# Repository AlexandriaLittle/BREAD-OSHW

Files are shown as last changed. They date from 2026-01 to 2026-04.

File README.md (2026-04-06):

# BREAD - Broadly Reconfigurable and Expandable Automation Device

## How to use
**Please check the Documentation folder for the original research paper and how-to guides!**

## Original Authors
The original project documentation is published in the open-access journal Hardware X 15 and is authored by Shane Oberloier, Nicholas G. Whisman, Finn Hafting, and Joshua M. Pearce. Other contributors have added to the body of work since. Please refer to the original sources (below) for important details about licensing, contributors, and any updates.

## About this repository
This is not an 'official' or even necessarily a current collection of all of these collected projects. Please see the links below to download from their original sources. The projects are collected here mostly for convenient access and learning.

## License
As the original project is licensed CC-BY-SA-4.0, this project is released under the same license. Social share image source https://www.appropedia.org/w/index.php?curid=122111.

## BREAD Links
- [Finn Hafting: Modularize your electronics with BREAD - YouTube](https://www.youtube.com/watch?v=OMPlVbqSqJ4)
- [Open Source Framework: Expandable Reconfigurable Data Acquisition Device (BREAD)](https://www.appropedia.org/Open_Source_Framework_for_a_Broadly_Expandable_and_Reconfigurable_Data_Acquisition_and_Automation_Device_(BREAD))
- [OSHE Bread Applications - Appropedia, the sustainability wiki](https://www.appropedia.org/OSHE_Bread_Applications)
- [GitHub - FHafting/BREAD](https://github.com/FHafting/BREAD)
- [OSF | BREAD](https://osf.io/u2h4g/overview)
- [OSF | LOAF_x04 Backplane](https://osf.io/7mk4w/overview)
- [OSF | BREAD LOAF_x08](https://osf.io/x4yqj/overview)
- [OSF | BREAD Slice - +/- 10A Current Sensor (SLC_CR10)](https://osf.io/ajmbe/overview)
- [OSF | BREAD Slice - +/- 20A Current Sensor (SLC_CR20)](https://osf.io/xe6cz/overview)
- [OSF | BREAD Slice - +/- 40A Current Sensor (SLC_CR40)](https://osf.io/xpgf8/overview)
- [OSF | BREAD Slice - 4 Channel Relay (SLC_RLAY)](https://osf.io/5vxws/overview)
- [OSF | BREAD Slice - Audio Analysis (SLC_AAFT)](https://osf.io/a8nk5/overview)
- [OSF | BREAD Slice - Bioreactor (SPECIALIZED) (SLC_PHDO)](https://osf.io/zbg98/overview)
- [OSF | BREAD Slice - BLDC Motor Controller](https://osf.io/w9rka/overview)
- [OSF | BREAD Slice - DC Motor Controller (SLC_DCMT)](https://osf.io/6aw9m/overview)
- [OSF | BREAD Slice - Field Solar Power (SLC_SOLR)](https://osf.io/9gm5h/overview)
- [OSF | BREAD Slice - MOLD(Mass Output and Logging Device)](https://osf.io/nm7je/overview)
- [OSF | BREAD Slice - Pressure Sensor](https://osf.io/86dz7/overview)
- [OSF | BREAD Slice - Pump Control Board (Specialized) (SLC_PUMP)](https://osf.io/4mzs8/overview)
- [OSF | BREAD Slice - Relay Heating Element Controller (SLC_RLHT)](https://osf.io/pf6gy/overview)
- [OSF | BREAD Slice - Servo Motor Controller (SLC_SERV)](https://osf.io/d7vks/overview)
- [OSF | BREAD Slice - Stepper Motor Controller (SLC_STEP)](https://osf.io/q8nkc/overview)
- [OSF | BREAD Slice - Template (SLC_TEMP)](https://osf.io/v5327/overview)
- [OSF | BREAD Slice - Text-to-Speech](https://osf.io/erbp6/overview)
- [OSF | BREAD Slice - Thermocouple Reader (SLC_THRM)](https://osf.io/sfehu/overview)
- [OSF | BREAD Slice - USB Port (SLC_USBP)](https://osf.io/j9rh5/overview)
- [OSF | BREAD Slice -- Analog Reader / FFT (SLC_LVAI)](https://osf.io/742ez/overview)
- [OSF | BREAD Slice -- Battery Management (SLC_BMS)](https://osf.io/yrmqu/overview)
- [OSF | BREAD Slice -- Buck Converter / Analog Signal Generator (SLC_BUCK)](https://osf.io/2xpnu/overview)
- [OSF | BREAD Slice-- Heating Element Controller (SLC_HEAT)](https://osf.io/m53fu/overview)
- [OSF | BREAD BUNS](https://osf.io/hbz92/overview)
- [OSF | BREAD CAN update](https://osf.io/3rnj4/overview)
- [OSF | BREAD DAQ](https://osf.io/wxt3s/overview)
- [OSF | BREAD Vision](https://osf.io/2htbm/overview)
- [OSF | Off-Grid BREAD](https://osf.io/98m6k/overview)
- [OSF | Integrated Open Source Pyrolysis Board based on BREAD](https://osf.io/3ugbn/overview)
- [Shane Oberloier | BREAD Contributor](https://osf.io/user/fntgd)
- [Nicholas Whisman | BREAD Contributor](https://osf.io/user/zs4mx?tab=2)
- [Finn Hafting | BREAD Contributor](https://osf.io/user/78mv4?tab=2)
- [BREAD References and Citations](https://ouci.dntb.gov.ua/en/works/lxXvAPQl/)
- [Open Source Hardware Enterprise](https://oshe.io/)
- [Original Project Logo](https://www.appropedia.org/w/index.php?curid=122111)

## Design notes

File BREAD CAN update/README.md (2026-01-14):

# BREAD Introduction

Welcome to the Broadly Reconfigurable and Expandable Automation Device (BREAD) project. This repository contains the files required to build your own supervisory control and data acquisition system or environmental sensing platform to suit your needs. Each function card, called a Slice, performs a specific function like temperature monitoring, DC motor control, relay control, etc. By linking Slices together with the Loaf backplane, you can create customized electronics to perform a variety of functions. This repository contains the bill of materials, board designs, 3D printable case design, and firmware examples for each Slice and the Loaf backplane.

## Navigating the repository

Each Slice and Loaf project is organized into the following files and subfolders:

-   Schematic.pdf: electrical schematic of the Slice in pdf format.
-   BOM_\<slice name\>.ods: bill of materials with links to purchase components on Digikey.
-   PCB Design: folder containing the KiCAD project files for the schematic and board design.
-   Gerbers: folder containing the gerber files extracted from the KiCAD board file. Use these files for manufacturing the PCB.
-   Firmware: folder containing examples and testing code unique to each Slice.
-   Mechanical: folder containing the 3D printable case files for each Slice.

## How to build a Slice

1.  Download all files from the Gerber folder. Compress files into a zip folder and upload to any PCB manufacturing company. If manufacturing the PCBs, use the “F_Cu.gbr” and “B_Cu.gbr” files for the front and back respectively.
2.  Order all components from the BOM file.
3.  Solder the components to the PCB starting with any SMD components and then through-hole components.
4.  3D print the case files using your favourite slicer.
5.  Assemble the case with the Slice hardware (finished PCB).

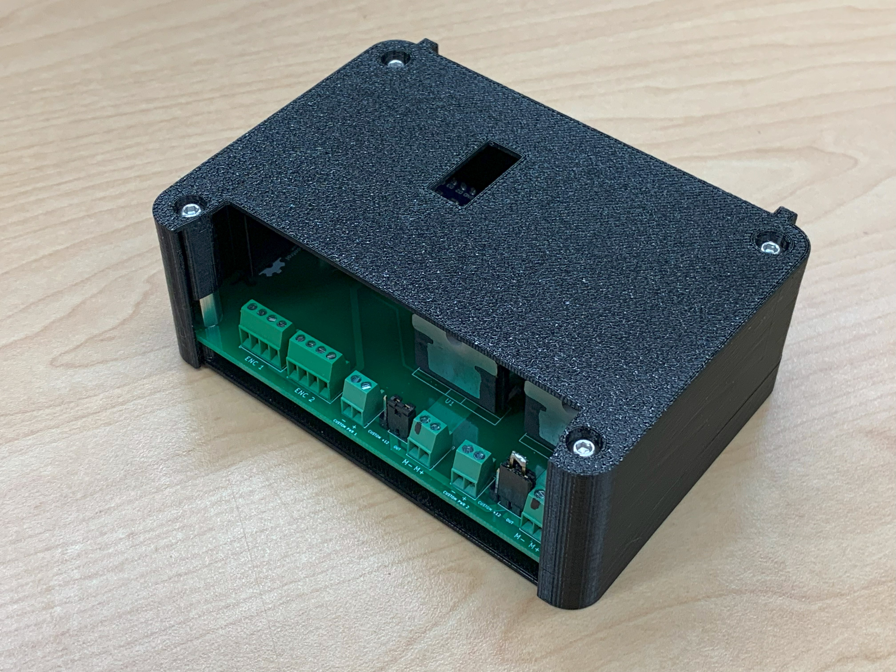
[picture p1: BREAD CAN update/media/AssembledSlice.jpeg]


## How to build the Loaf

Follow the same steps as the Slice; however, the case takes more steps to assemble.

1.  Use hot glue to assemble the 2 bottom pieces and 2 top pieces of the case.

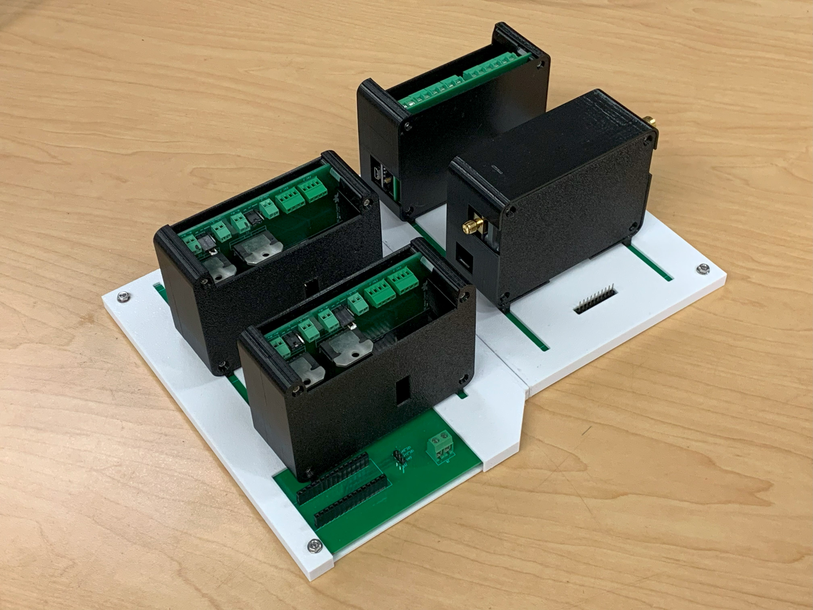
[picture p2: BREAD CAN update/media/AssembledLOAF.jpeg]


## Using the template to design new Slices

The template project (SLC_TEMP) provides a starting KiCAD project with the standard Slice components. The components should remain untouched, and designers should work around them when designing new Slices. Once finished with the board design, edit the Slice name, description, and version number to reflect the new Slice characteristics.

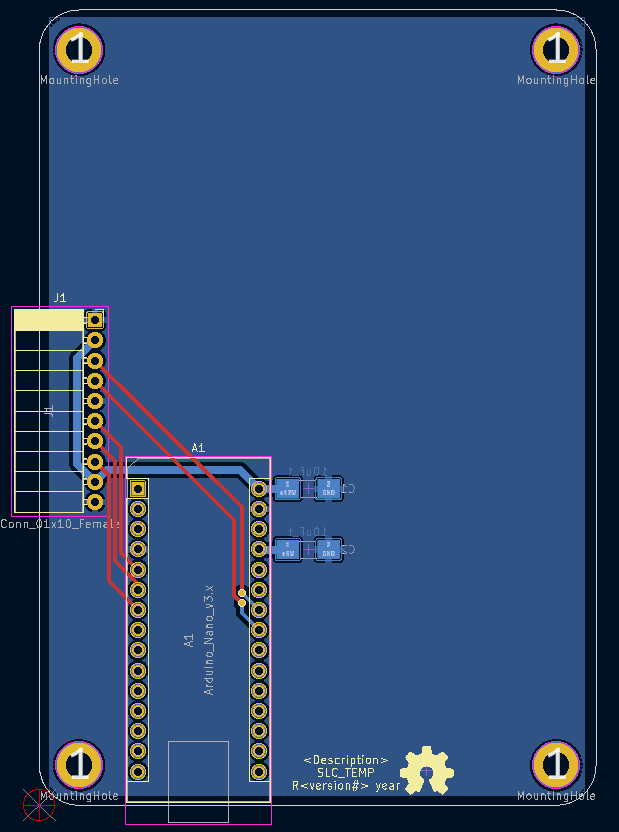
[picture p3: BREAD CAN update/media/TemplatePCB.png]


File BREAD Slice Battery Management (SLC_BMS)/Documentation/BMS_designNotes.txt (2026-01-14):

This slice is made up of two main sections:

Solar Charger: "Adafruit Universal USB / DC / Solar Lithium Ion/Polymer charger" based on bq24074
Boost Converter: Based on MT3608

Solar Charger Changes from Adafruit Design:
	removed output connector and assosiated capacitors
	output goes to input of boost converter
	two capacitors on OUT pin are unpopulated, and are there incase more capacitance is necessary.
	two single-pin headers are for extra capacitor? Part of adafruit design. Removed.
	replaced USB C connector with micro USB connector USB3076-30-A from GCT, footprint in KiCad libraries	
	Status indicating LEDs are driven by arduino, arduino reads status from bq24074 and updates LEDs
	
Boost Converter Notes:
	steps ~4.4V output of solar charger up to 12V and outputs to loaf
	components salvaged from MT3608 converter from amazon, no cheap/suitable options found on DigiKey
	If MT3608 can't be found, any 4V-12V DC-DC converter should work as replacement
	MT3608 footprint in KiCad libraries
	Net "OUT" on boost converter is the input. It's the output of the solar charging chip

Arduino pins:
	D5	|	~CHG	|	pulled to GND when battery is charging - use internal pullup on arduino. pinMode(5, INPUT_PULLUP);
	D6	|	~PGOOD	|	pulled to GND when valid power source is connected - use internal pullup
	D7	|	CHGI	|	High when ~CHG is low, used to drive status LED
	D8	|	PGOODI	|	High when ~PGOOD is low, used to drive status LED
	A0	|	ISET	|	Use to monitor actual charging current, see bq24074 datasheet for details
	
Other headers:
	THERM/GND	|	used to connect ntc thermistor on battery pack. Ignore this header unless you need to use it,
					in which case be sure to break connection on solder jumper THERM1

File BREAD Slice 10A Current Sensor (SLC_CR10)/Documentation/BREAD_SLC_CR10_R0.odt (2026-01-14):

# Broadly Reconfigurable and Expandable Automation Device (BREAD) – Slice Datasheet: 10A Current Sensor Slice (SLC-CR10)

By: Nicholas Whisman (ngwhisma@mtu.edu) – Revision 0, on 17. May 2021

## Short Device Description

This slice acts as a current sensor, and is rated for up to ±10 Amps. The sensor outputs a voltage signal linearly related to the current flowing through the chip, at an approximate resolution of 200 mV / Amp.

## Quick Information

Device at a Glance

Short title | 10A Current Detector
Part # | SLC-CR10
Repository Link | Link to OSF or other repository
Academic Paper DOI | DOI link to published paper
Device Cost | Monetary cost of the device
Assembly Difficulty | Medium. Millable.
Application Area | Power Analysis, Controls

Device Connections

Current Input Screw Terminals

Pin # | Description | Rating
J2 | Screw terminal connection points for desired current to measure. Positive lead connects to right side of terminal. | 10A
J3 | Screw terminal connection points for desired current to measure. Positive lead connects to right side of terminal. | 10A
J4 | Screw terminal connection points for desired current to measure. Positive lead connects to right side of terminal. | 10A
J5 | Screw terminal connection points for desired current to measure. Positive lead connects to right side of terminal. | 10A

## Commands

Setup (no significant returns)
Byte: Address | Bit: 1 | Float: Target Temp | Float: Ramp Rate (d/m)
Read Current (returns the current through the selected channel)
Byte: Address | Bit: 0 | Float: 0 | Float: 0

## Schematic

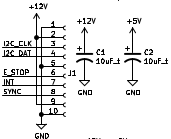
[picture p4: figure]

Figure 1: BREAD Connection Pins + Power Capacitors

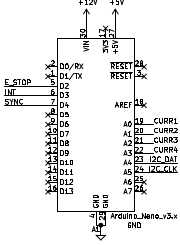
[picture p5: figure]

Figure 2: Arduino Nano

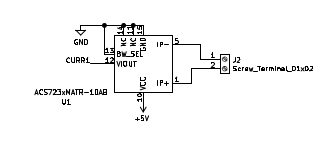
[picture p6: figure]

Figure 3: One of four identical current sensing channels

## Bill of Materials

Designator | Description | Quantity | Cost / part | URL
U1-4 | 10A Current Sensor Chip | 4 | 5.68 | https://www.digikey.com/en/products/detail/allegro-microsystems/ACS723KMATR-10AB-T/5225374
J2-J5 | 1/10” Pitch 01x02 Screw Terminals | 4 | 1.27 | https://www.digikey.com/en/products/detail/te-connectivity-amp-connectors/282834-2/1150135
C1-2 | 1206 Packaging 10 µF Capacitor | 2 | 0.64 | https://www.digikey.com/short/qfrbqfhd
A1 | Arduino Nano | 1 | 22.00 | https://www.digikey.com/en/products/detail/arduino/A000005/2638989
J1 | 01x10 Female Header Pins | 1 | 0.79 | https://www.digikey.com/short/23bfwwjh

## Construction & Fabrication

List any tools that are required and short guide on the order which parts should be soldered / assembled. Be sure to note any specialized methods and point out components that may easily be soldered in the incorrect orientation. Additionally include at least one picture of the assembled board (include both sides if there are components on both sides).

[Image of the assembled Circuit Board]

Fig #. Subtitle should go here.

## Configuration & Calibration

Include a list of default jumper and potentiometer positions:

Hardware Positions

- Turn P1 to be roughly 50%
- Turn P2 to be completely closed (turn clockwise until potentiometer clicks)
- Place a jumper to short out J3. Etc…

Detail any key parameters the end-user may want to adjust in the firmware, and if there are any special instructions before programming the Slice.

Tools Required For Calibration

- An oscilloscope with at least 15Mhz sampling
- A multimeter. Etc…

List all of the tools / instruments required for calibration. Provide a detailed & step by step guide on how to calibrate (or validate) each unique type of channel on the card. Include what variables in the firmware may need to be adjusted (and when). Attach a wiring diagram for each relevant calibration circuit.

[Image of the calibration circuit]

Fig #. Subtitle should go here.

## Usage & Constraints

List the relevant constraints for each type of channel on the card. These parameters may be quantities like max current, max voltage, frequency, sampling frequency, etc.

List an example wiring diagram of the slice in use, as well as some suggested applications

[Image of the example usage wiring diagram]

Fig #. Subtitle should go here.

## General Comments on Slice

This section is intended as a catch-all for any topics that are relevant to the Slice that don’t fit in any other category.

## Revision Notes

- Rev 0 – Initial document release (DATE HERE)

SLC-CR10 Datasheet – Revision 0

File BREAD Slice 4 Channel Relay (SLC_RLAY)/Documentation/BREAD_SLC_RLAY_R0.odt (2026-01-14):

# Broadly Reconfigurable and Expandable Automation Device (BREAD) – Slice Datasheet: Relay Slice (SLC-RLAY)

By: Nicholas Whisman (ngwhisma@mtu.edu) – Revision 0, on 17. May 2021

## Short Device Description

This device controls 4 relay channels via the Arduino, and receives analog signals (optionally) as feedback.

## Quick Information

Device at a Glance

Short title | Relay Slice
Part # | SLC-RLAY
Repository Link | Link to OSF or other repository
Academic Paper DOI | DOI link to published paper
Device Cost | Monetary cost of the device
Assembly Difficulty | Medium. Millable.
Application Area | Controls, Power Monitoring

Device Connections

J2 – Relay Output 1

Pin # | Description | Rating
1 | Normally closed switch of relay | 277 VAC, 30V DC, 3A
2 | Normally open switch of relay | 277 VAC, 30V DC, 10A AC, 5A DC
3 | Common pin | N/A

J2 – Relay Output 2

Pin # | Description | Rating
1 | Normally closed switch of relay | 277 VAC, 30V DC, 3A
2 | Normally open switch of relay | 277 VAC, 30V DC, 10A AC, 5A DC
3 | Common pin | N/A

J2 – Relay Output 3

Pin # | Description | Rating
1 | Normally closed switch of relay | 277 VAC, 30V DC, 3A
2 | Normally open switch of relay | 277 VAC, 30V DC, 10A AC, 5A DC
3 | Common pin | N/A

J2 – Relay Output 4

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

## Commands

Write Switch(es) (no significant returns)
Byte: Address | Bit: 1 | Float: Target Temp | Float: Ramp Rate (d/m)
Timed Write (no significant returns)
Byte: Address | Bit: 0 | Float: 0 | Float: 0
Analog Read (Returns selected voltages from analog feedback)

## Schematic

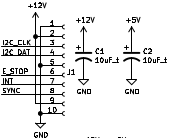
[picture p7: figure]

Figure 1: BREAD Connection Port + Power Capacitors

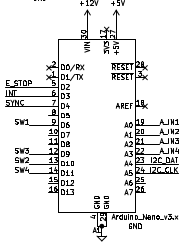
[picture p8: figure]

Figure 2: Arduino Nano

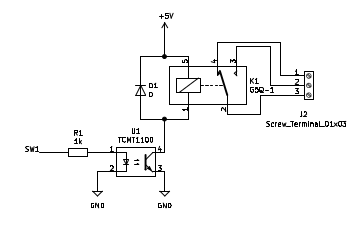
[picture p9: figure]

Figure 3: One of Four Relay Channels

Figure 4: One of Four Analog Input Paths

Figure 5: Feedback Input Port

## Bill of Materials

Designator | Description | Quantity | Cost / part | URL
U1-4 | Optocouplers | 4 | 0.51 | https://www.digikey.com/short/5fmc702d
RV1-4 | 10k Trimmer Potentiometer | 4 | 4.16 | https://www.digikey.com/short/ftm98v7t
R1-4 | 1k 1206 Packaging Resistor | 4 | 0.1 | https://www.digikey.com/short/d1dmzmbb
K1-4 | G5Q1 SPDT Relay | 4 | 1.52 | https://www.digikey.com/short/vj4jr0vq
J6 | 01x04 1/10” Pitch Terminal Block | 1 | 2.75 | https://www.digikey.com/short/rnm0hhhn
J2-5 | 01x03 1/10” Pitch Terminal Block | 4 | 2.06 | https://www.digikey.com/short/71d77cj2
D5-8 | 5.1V Zener Diode | 4 | 0.22 | https://www.digikey.com/short/tvbtwpmt
D1-4 | Standard THT Diode | 4 | 0.21 | https://www.digikey.com/short/tp4mrn5q
C1-2 | 10 µF 1206 Packaging Ceramic Capacitor | 4 | 0.64 | https://www.digikey.com/short/2ffb0248
A1 | Arduino Nano | 1 | 22.00 | https://www.digikey.com/en/products/detail/arduino/A000005/2638989
J1 | 01x10 Female Header Pins | 1 | 0.79 | https://www.digikey.com/short/23bfwwjh

## Construction & Fabrication

List any tools that are required and short guide on the order which parts should be soldered / assembled. Be sure to note any specialized methods and point out components that may easily be soldered in the incorrect orientation. Additionally include at least one picture of the assembled board (include both sides if there are components on both sides).

[Image of the assembled Circuit Board]

Fig #. Subtitle should go here.

## Configuration & Calibration

Include a list of default jumper and potentiometer positions:

Hardware Positions

- Turn P1 to be roughly 50%
- Turn P2 to be completely closed (turn clockwise until potentiometer clicks)
- Place a jumper to short out J3. Etc…

Detail any key parameters the end-user may want to adjust in the firmware, and if there are any special instructions before programming the Slice.

Tools Required For Calibration

- An oscilloscope with at least 15Mhz sampling
- A multimeter. Etc…

List all of the tools / instruments required for calibration. Provide a detailed & step by step guide on how to calibrate (or validate) each unique type of channel on the card. Include what variables in the firmware may need to be adjusted (and when). Attach a wiring diagram for each relevant calibration circuit.

[Image of the calibration circuit]

Fig #. Subtitle should go here.

## Usage & Constraints

List the relevant constraints for each type of channel on the card. These parameters may be quantities like max current, max voltage, frequency, sampling frequency, etc.

List an example wiring diagram of the slice in use, as well as some suggested applications

[Image of the example usage wiring diagram]

Fig #. Subtitle should go here.

## General Comments on Slice

This section is intended as a catch-all for any topics that are relevant to the Slice that don’t fit in any other category.

## Revision Notes

- Rev 0 – Initial document release (DATE HERE)

SLC-RLAY Datasheet – Revision 0

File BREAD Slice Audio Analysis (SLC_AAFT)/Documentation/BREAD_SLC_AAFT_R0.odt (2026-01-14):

# Broadly Reconfigurable and Expandable Automation Device (BREAD) – Slice Datasheet: Audio Analysis / Fourier Transform Slice

By: Nicholas Whisman (ngwhisma@mtu.edu) – Revision 0, on 17. May 2021

## Short Device Description

This device takes in an audio signal from either an Aux cable or a quarter inch cable, and shifts, amplifies, and breaks down the signal into constituent frequency ranges. These ranges, or the full signal, can then be analyzed via fast Fourier transform.

## Quick Information

Device at a Glance

Short title | Audio Analysis / Fourier Transform Slice
Part # | SLC-AAFT
Repository Link | Link to OSF or other repository
Academic Paper DOI | DOI link to published paper
Device Cost | Monetary cost of the device
Assembly Difficulty | Medium. Millable.
Application Area | Controls + Robotics (Vibrational/Tonal Sensing + Correction), Limited Frequency Range Audio

Device Connections

J2- Aux

Pin # | Description | Rating
1 | A standard aux cord used for personal electronic devices. | Standard aux cord protocol is to set maximum possible voltage at ~ 0.477 V. Plan accordingly with amplifier configuration to not exceed 5V total.

J3- Quarter Inch

Pin # | Description | Rating
1 | Quarter Inch jack used in professional audio settings. | Quarter Inch jacks typically output 1.736 V at a maximum. Plan amplifier tweaks accordingly.

## Commands

Set Up (no significant returns)
Byte: Address | Bit: 1 | Float: Target Temp | Float: Ramp Rate (d/m)
Read (Returns Magnitudes of Specified Bins)
Byte: Address | Bit: 0 | Float: 0 | Float: 0
Stat Read (Returns Requested Statistic)
Byte: Address | Bit: 0 | Float: 0 | Float: 0

## Schematic

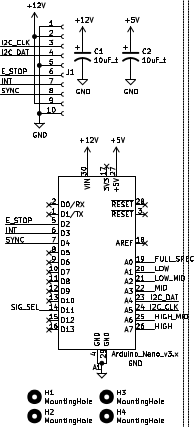
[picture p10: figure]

Figure 1: Standard Core Slice Components

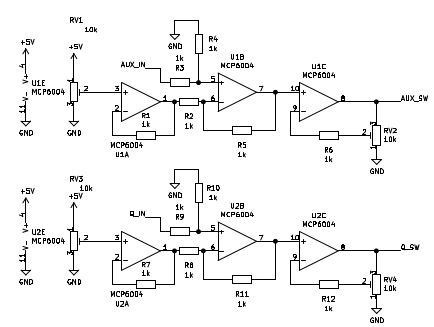
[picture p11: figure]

Figure 2: Aux + Quarter Inch Channel Amps

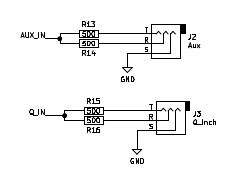
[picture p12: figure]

Figure 3: Aux and Quarter Inch Inputs

Figure 4: Signal Transfer Bridge

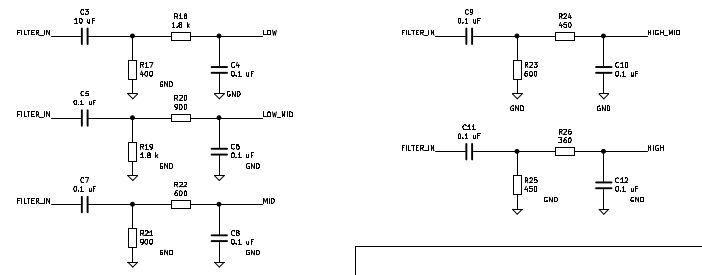
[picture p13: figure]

Figure 5: Range Filters

## Bill of Materials

Designator | Description | Quantity | Cost / part | URL
U1-2 | 4 Stage Amplifier Chip | 2 | 0.44 | https://www.digikey.com/en/products/detail/microchip-technology/MCP6004T-I-ST/523078
J2 | Aux Cord Jack | 1 | 1.18 | https://www.digikey.com/en/products/detail/cui-devices/SJ1-3533NG/738701
RV1-4 | 10k 12 Turn Trim Pot | 4 | 4.16 | https://www.digikey.com/en/products/detail/bourns-inc/3266W-1-103LF/1087907
R26 | 1206 Packaging 360Ω Resistor | 1 | 0.10 | https://www.digikey.com/en/products/detail/yageo/AC1206FR-07360RL/5897483
R24-25 | 1206 Packaging 450Ω Resistor | 2 | 0.10 | https://www.digikey.com/en/products/detail/yageo/RC1206FR-07453RL/728924
R22-23 | 1206 Packaging 600Ω Resistor | 2 | 0.10 | https://www.digikey.com/en/products/detail/yageo/RC1206FR-07604RL/729038
R20-21 | 1206 Packaging 900Ω Resistor | 2 | 0.10 | https://www.digikey.com/en/products/detail/yageo/RC1206FR-07909RL/729166
R18-19 | 1206 Packaging 1.8 kΩ Resistor | 2 | 0.10 | https://www.digikey.com/en/products/detail/yageo/RC1206JR-071K8L/729204
R17 | 1206 Packaging 400Ω Resistor | 1 | 0.10 | https://www.digikey.com/en/products/detail/yageo/RT1206BRD07400RL/5936956
R13-16 | 1206 Packaging 500Ω Resistor | 4 | 0.10 | https://www.digikey.com/en/products/detail/yageo/RC1206FR-07499RL/728944
R1-12 | 1206 Packaging 1 kΩ Resistor | 12 | 0.10 | https://www.digikey.com/en/products/detail/yageo/RC1206FR-071KL/728387
J3 | Quarter Inch Jack | 1 | 1.58 | https://www.mouser.com/ProductDetail/Neutrik/NMJ6HCD2?qs=ZNZTMDotSRlKYl2qFVJbQA%3D%3D
C4-12 | 1206 Packaging 0.1 µF Capacitor | 9 | 0.16 | https://www.digikey.com/en/products/detail/yageo/CC1206KRX7R8BB104/5884627
C3 | 1206 Packaging 10 µF Capacitor | 1 | 0.66 | https://www.digikey.com/en/products/detail/yageo/CC1206KKX5R6BB106/5195344
C1-2 | 1206 Packaging 10 µF Capacitor | 2 | 0.64 | https://www.digikey.com/short/qfrbqfhd
A1 | Arduino Nano | 1 | 22.00 | https://www.digikey.com/en/products/detail/arduino/A000005/2638989
J1 | 01x10 Female Header Pins | 1 | 0.79 | https://www.digikey.com/short/23bfwwjh

## Construction & Fabrication

List any tools that are required and short guide on the order which parts should be soldered / assembled. Be sure to note any specialized methods and point out components that may easily be soldered in the incorrect orientation. Additionally include at least one picture of the assembled board (include both sides if there are components on both sides).

[Image of the assembled Circuit Board]

Fig #. Subtitle should go here.

## Configuration & Calibration

Include a list of default jumper and potentiometer positions:

Hardware Positions

- Turn P1 to be roughly 50%
- Turn P2 to be completely closed (turn clockwise until potentiometer clicks)
- Place a jumper to short out J3. Etc…

Detail any key parameters the end-user may want to adjust in the firmware, and if there are any special instructions before programming the Slice.

Tools Required For Calibration

- An oscilloscope with at least 15Mhz sampling
- A multimeter. Etc…

List all of the tools / instruments required for calibration. Provide a detailed & step by step guide on how to calibrate (or validate) each unique type of channel on the card. Include what variables in the firmware may need to be adjusted (and when). Attach a wiring diagram for each relevant calibration circuit.

[Image of the calibration circuit]

Fig #. Subtitle should go here.

## Usage & Constraints

List the relevant constraints for each type of channel on the card. These parameters may be quantities like max current, max voltage, frequency, sampling frequency, etc.

List an example wiring diagram of the slice in use, as well as some suggested applications

[Image of the example usage wiring diagram]

Fig #. Subtitle should go here.

## General Comments on Slice

This section is intended as a catch-all for any topics that are relevant to the Slice that don’t fit in any other category.

## Revision Notes

- Rev 0 – Initial document release (DATE HERE)

SLC-AAFT Datasheet – Revision 0

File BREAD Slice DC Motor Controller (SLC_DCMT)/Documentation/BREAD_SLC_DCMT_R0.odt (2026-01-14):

# Broadly Reconfigurable and Expandable Automation Device (BREAD) – Slice Datasheet: DC Motor Control Slice (SLC-DCMT)

By: Nicholas Whisman (ngwhisma@mtu.edu) – Revision 0, on 17. May 2021

## Short Device Description

This slice is designed to control two DC motors. The main control is through a H-Bridge chip, and the system feedback is received via rotary encoder.

## Quick Information

Device at a Glance

Short title | DC Motor Control Slice
Part # | SLC-DCMT
Repository Link | Link to OSF or other repository
Academic Paper DOI | DOI link to published paper
Device Cost | Monetary cost of the device
Assembly Difficulty | Difficult. Millable.
Application Area | Machinery Control, Robotics

Device Connections

J2 – Rotary Encoder Input

Pin # | Description | Rating
1 | Signal A | N/A
2 | Signal B | N/A
3 | +5V | N/A
4 | GND | N/A

J3 – Rotary Encoder Input

Pin # | Description | Rating
1 | Signal A | N/A
2 | Signal B | N/A
3 | +5V | N/A
4 | GND | N/A

J4 – Motor 1 Power Select

Pin # | Description | Rating
1 | Custom Power Pin | 55V
2 | +12V Standard | N/A
3 | Feed to H-Bridge / Motor | One of the above pins MUST be connected to this feed pin for the system to operate.

J5 – Motor 2 Power Select

Pin # | Description | Rating
1 | Custom Power Pin | 55V
2 | +12V Standard | N/A
3 | Feed to H-Bridge / Motor | One of the above pins MUST be connected to this feed pin for the system to operate.

J6 – Feed to Motor

Pin # | Description | Rating
1 | Motor + | Use current sense functionality to ensure safety for individual motors.
2 | Motor - | Use current sense functionality to ensure safety for individual motors.

J7 – Feed to Motor

Pin # | Description | Rating
1 | Motor + | Use current sense functionality to ensure safety for individual motors.
2 | Motor - | Use current sense functionality to ensure safety for individual motors.

J8 – Custom Power Input

Pin # | Description | Rating
1 | +V | Max of 55V
2 | GND | N/A

J9 – Custom Power Input

Pin # | Description | Rating
1 | +V | Max of 55V
2 | GND | N/A

## Commands

Write Power (no significant returns)
Byte: Address | Bit: 1 | Float: | Float:
Write Speed (no significant returns)
Byte: Address | Bit: 0 | Float: 0 | Float: 0
Brake (no significant returns)
Byte: Address | Bit: 0 | Float: 0 | Float: 0
Write Direction (no significant returns)
Byte: Address | Bit: 0 | Float: 0 | Float: 0
Read Current (returns detected current through the motors)
Byte: Address | Bit: 0 | Float: 0 | Float: 0
Read Thermal Flag (returns current value of thermal flag)
Byte: Address | Bit: 0 | Float: 0 | Float: 0
Setup (no significant returns)
Byte: Address | Bit: 0 | Float: 0 | Float: 0

## Schematic

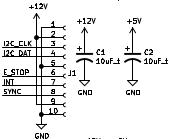
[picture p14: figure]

Figure 1: BREAD Connection Point and Power Capacitors

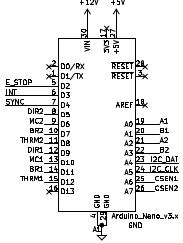
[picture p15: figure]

Figure 2: Arduino Nano

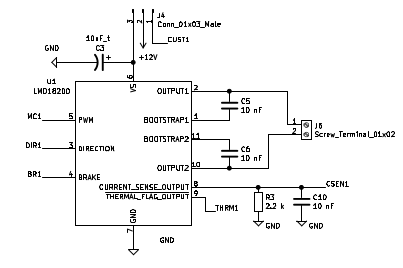
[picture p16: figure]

Figure 3: One of two H-Bridge channels

Figure 4: One of two custom power inputs

Figure 5: One of two rotary encoder inputs

## Bill of Materials

Designator | Description | Quantity | Cost / part | URL
C5-10 | 10 nF 1206 Packaging Ceramic Capacitor | 6 | 0.24 | https://www.digikey.com/en/products/detail/yageo/CC1206KRX7R9BB103/302908
C1-4 | 10 µF 1206 Packaging Ceramic Capacitor | 4 | 0.64 | https://www.digikey.com/short/2ffb0248
A1 | Arduino Nano | 1 | 22.00 | https://www.digikey.com/en/products/detail/arduino/A000005/2638989
R3-4 | 2.2k 1206 Packaging Resistor (±0.1%) | 2 | 0.62 | https://www.digikey.com/en/products/detail/yageo/RT1206BRD072K2L/1079707
J6-9 | 01x02 1/10” Pitch Terminal Blocks | 4 | 1.27 | https://www.digikey.com/short/72hnmwd5
J4-5 | 01x03 1/10” Pitch Terminal Blocks | 2 | 2.06 | https://www.digikey.com/short/70279tb0
J2-3 | 01x04 1/10” Pitch Terminal Blocks | 2 | 2.75 | https://www.digikey.com/short/bftjz0bt

## Construction & Fabrication

List any tools that are required and short guide on the order which parts should be soldered / assembled. Be sure to note any specialized methods and point out components that may easily be soldered in the incorrect orientation. Additionally include at least one picture of the assembled board (include both sides if there are components on both sides).

[Image of the assembled Circuit Board]

Fig #. Subtitle should go here.

## Configuration & Calibration

Include a list of default jumper and potentiometer positions:

Hardware Positions

- Turn P1 to be roughly 50%
- Turn P2 to be completely closed (turn clockwise until potentiometer clicks)
- Place a jumper to short out J3. Etc…

Detail any key parameters the end-user may want to adjust in the firmware, and if there are any special instructions before programming the Slice.

Tools Required For Calibration

- An oscilloscope with at least 15Mhz sampling
- A multimeter. Etc…

List all of the tools / instruments required for calibration. Provide a detailed & step by step guide on how to calibrate (or validate) each unique type of channel on the card. Include what variables in the firmware may need to be adjusted (and when). Attach a wiring diagram for each relevant calibration circuit.

[Image of the calibration circuit]

Fig #. Subtitle should go here.

## Usage & Constraints

List the relevant constraints for each type of channel on the card. These parameters may be quantities like max current, max voltage, frequency, sampling frequency, etc.

List an example wiring diagram of the slice in use, as well as some suggested applications

[Image of the example usage wiring diagram]

Fig #. Subtitle should go here.

## General Comments on Slice

This section is intended as a catch-all for any topics that are relevant to the Slice that don’t fit in any other category.

## Revision Notes

- Rev 0 – Initial document release (DATE HERE)

SLC-DCMT Datasheet – Revision 0

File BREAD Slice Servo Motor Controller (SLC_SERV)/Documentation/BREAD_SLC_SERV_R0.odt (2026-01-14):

# Broadly Reconfigurable and Expandable Automation Device (BREAD) – Slice Datasheet: Servo Motor Control Slice (SLC-SERV)

By: Nicholas Whisman (ngwhisma@mtu.edu) – Revision 0, on 18. May 2021

## Short Device Description

This device controls up to 5 Servo motors. As Servo motors have internal feedback control systems, this system thus has no feedback path.

## Quick Information

Device at a Glance

Short title | Servo Motor Control Slice
Part # | SLC-SERV
Repository Link | Link to OSF or other repository
Academic Paper DOI | DOI link to published paper
Device Cost | Monetary cost of the device
Assembly Difficulty | Easy, Millable
Application Area | Robotics, Controlling Machinery

Device Connections

J2 – Servo Motor 1

Pin # | Description | Rating
1 | PWM to Servo | N/A
2 | Voltage Input | Varies by Motor. Terminal can only support 10-15A
3 | GND | N/A

J3 – Servo Motor 2

Pin # | Description | Rating
1 | PWM to Servo | N/A
2 | Voltage Input | Varies by Motor. Terminal can only support 10-15A
3 | GND | N/A

J4 – Servo Motor 3

Pin # | Description | Rating
1 | PWM to Servo | N/A
2 | Voltage Input | Varies by Motor. Terminal can only support 10-15A
3 | GND | N/A

J5 – Servo Motor 4

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

J6 – Servo Motor 5

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

J7 – Power Select

Pin # | Description | Rating
1 | Power Output Pin | MUST connect one of the below to this pin.
2 | Custom Power Input | N/A
3 | Standard 12V | N/A

J8 – Custom Power Input

Pin # | Description | Rating
1 | V + | N/A
2 | GND | N/A

## Commands

Write Angle (no significant returns)
Byte: Address | Bit: 1 | Float: Target Temp | Float: Ramp Rate (d/m)
Set Up (no significant returns)
Byte: Address | Bit: 0 | Float: 0 | Float: 0

## Schematic

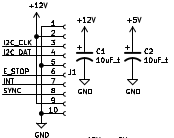
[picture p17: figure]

Figure 1: BREAD Connection Port and Power Capacitors

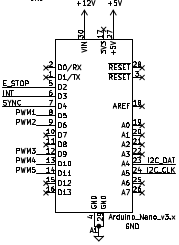
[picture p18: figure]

Figure 2: Arduino Nano

Figure 3: One of five identical Servo connection ports

Figure 4: Power Select Pins

Figure 5: Custom Power Input Port

## Bill of Materials

Designator | Description | Quantity | Cost / part | URL
J8 | 01x02 1/10” Pitch Terminal Block | 1 | 1.27 | https://www.digikey.com/short/792dvv77
J7 | 01x03 1/10” Pitch Connector Pins | 1 | 0.27 | https://www.digikey.com/short/2j42vf3d
J2-J6 | 01x03 1/10” Pitch Terminal Block | 5 | 2.06 | https://www.digikey.com/short/18bph2rj
J1 | 01x10 Female Header Pins | 1 | 0.79 | https://www.digikey.com/short/23bfwwjh
C1-2 | 1206 Packaging 10 µF Capacitor | 2 | 0.64 | https://www.digikey.com/short/qfrbqfhd
A1 | Arduino Nano | 1 | 22.00 | https://www.digikey.com/en/products/detail/arduino/A000005/2638989

## Construction & Fabrication

List any tools that are required and short guide on the order which parts should be soldered / assembled. Be sure to note any specialized methods and point out components that may easily be soldered in the incorrect orientation. Additionally include at least one picture of the assembled board (include both sides if there are components on both sides).

[Image of the assembled Circuit Board]

Fig #. Subtitle should go here.

## Configuration & Calibration

Include a list of default jumper and potentiometer positions:

Hardware Positions

- Turn P1 to be roughly 50%
- Turn P2 to be completely closed (turn clockwise until potentiometer clicks)
- Place a jumper to short out J3. Etc…

Detail any key parameters the end-user may want to adjust in the firmware, and if there are any special instructions before programming the Slice.

Tools Required For Calibration

- An oscilloscope with at least 15Mhz sampling
- A multimeter. Etc…

List all of the tools / instruments required for calibration. Provide a detailed & step by step guide on how to calibrate (or validate) each unique type of channel on the card. Include what variables in the firmware may need to be adjusted (and when). Attach a wiring diagram for each relevant calibration circuit.

[Image of the calibration circuit]

Fig #. Subtitle should go here.

## Usage & Constraints

List the relevant constraints for each type of channel on the card. These parameters may be quantities like max current, max voltage, frequency, sampling frequency, etc.

List an example wiring diagram of the slice in use, as well as some suggested applications

[Image of the example usage wiring diagram]

Fig #. Subtitle should go here.

## General Comments on Slice

This section is intended as a catch-all for any topics that are relevant to the Slice that don’t fit in any other category.

## Revision Notes

- Rev 0 – Initial document release (DATE HERE)

SLC-SERV Datasheet – Revision 0

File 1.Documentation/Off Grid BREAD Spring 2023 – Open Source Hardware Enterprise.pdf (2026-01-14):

# Off Grid BREAD Spring 2023

Home (https://oshe.io) / Semester Reports (https://oshe.io/category/semester-reports/) / Off Grid BREAD Spring 2023 (https://oshe.io/post/920/off-grid-bread-spring-2023/)

(https://openhardware.eit.mtu.edu)

## Open Source Hardware Enterprise

Home (https://oshe.io/)
The OSHE Team (https://oshe.io/team/) Upcoming Events (https://oshe.io/upcoming-events/) Project Overviews (https://oshe.io/project-overviews/)

# Off Grid BREAD Spring 2023

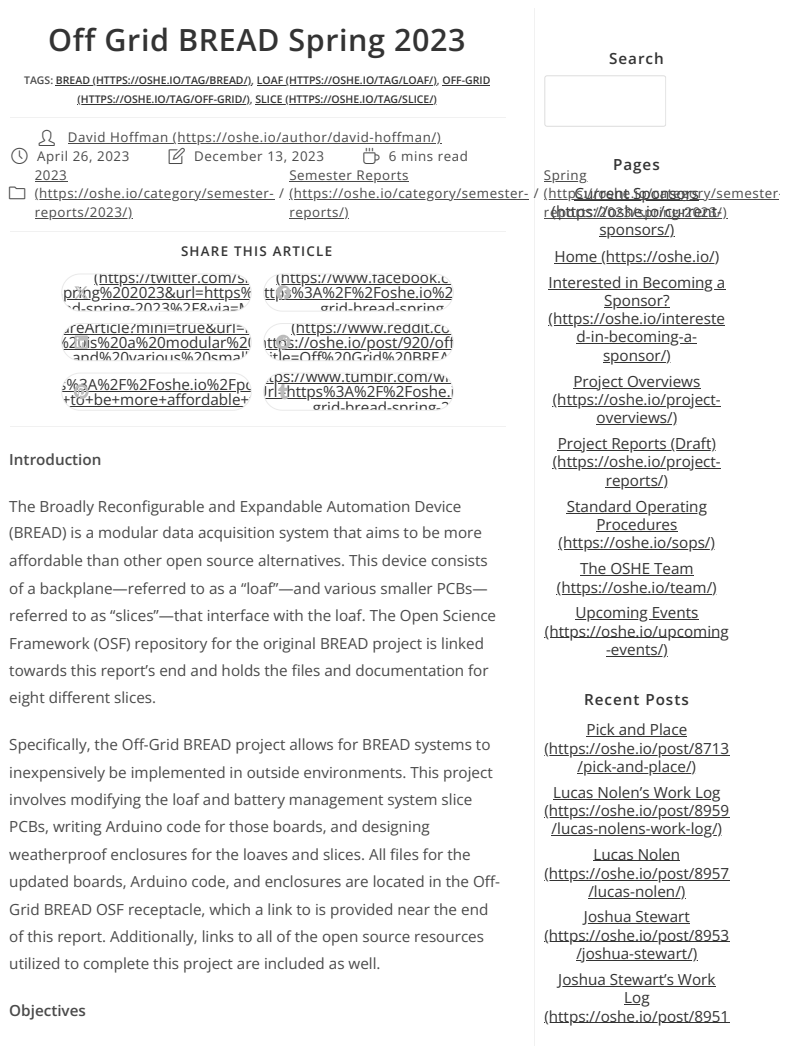
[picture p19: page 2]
Search; -events/); Log; April 26, 2023; December 13, 2023; 6 mins read; Semester Reports; reports/); Introduction; Objectives

TAGS: BREAD (HTTPS://OSHE.IO/TAG/BREAD/), LOAF (HTTPS://OSHE.IO/TAG/LOAF/), OFF-GRID

(HTTPS://OSHE.IO/TAG/OFF-GRID/), SLICE (HTTPS://OSHE.IO/TAG/SLICE/)

David Hoffman (https://oshe.io/author/david-hoffman/)
(https://oshe.io/category/semester-
reports/2023/) (https://oshe.io/category/semester-reports/2023/)

Pages
Current Sponsors
(https://oshe.io/current-
r (https://oshe.io/category/semester-reports/2023/spring-2023/)eports/2023/spring-2023/ (https://oshe.io/current-sponsors/)) (https://oshe.io/category/semester-reports/2023/spring-2023/)
sponsors/) (https://oshe.io/current-sponsors/)
Home (https://oshe.io/)
Interested in Becoming a
Sponsor?
(https://oshe.io/intereste
d-in-becoming-a-
sponsor/) (https://oshe.io/interested-in-becoming-a-sponsor/)
Project Overviews
(https://oshe.io/project-
overviews/) (https://oshe.io/project-overviews/)
Project Reports (Draft)
reports/) (https://oshe.io/project-reports/)
Standard Operating
Procedures
(https://oshe.io/sops/)
The OSHE Team
(https://oshe.io/team/)
Upcoming Events
(https://oshe.io/upcoming

Spring
(https://oshe.io/catego (https://oshe.io/current-sponsors/)ry/semester-

SHARE THIS ARTICLE

(https://twitter.com/sh (https://twitter.com/share?text=Off%20Grid%20BREAD%20Spring%202023&via=MTU_OpenSource)
Spring%202023&url=https% (https://twitter.com/share?text=Off%20Grid%20BREAD%20Spring%202023&via=MTU_OpenSource)
ead-spring-2023%2F&via=M (https://twitter.com/share?text=Off%20Grid%20BREAD%20Spring%202023&via=MTU_OpenSource)
areArticle?mini=true&url=h
%20is%20a%20modular%20
—and%20various%20smalle (https://www.linkedin.com/shareArticle?mini=true&title=Off%20Grid%20BREAD%20Spring%202023)
s%3A%2F%2Foshe.io%2Fpo
+to+be+more+affordable+t (https://www.pinterest.com/pin/create/button/)

(https://www.facebook.co
ttps%3A%2F%2Foshe.io%2
grid-bread-spring-2 (https://www.facebook.com/sharer.php)
(https://www.reddit.com (https://www.reddit.com/submit?title=Off%20Grid%20BREAD%20Spring%202023)
https://oshe.io/post/920/off
title=Off%20Grid%20BREAD (https://www.reddit.com/submit?title=Off%20Grid%20BREAD%20Spring%202023)
ttps://www.tumblr.com/wid (https://www.tumblr.com/widgets/share/tool)
Url=https%3A%2F%2Foshe.i
grid-bread-spring-20 (https://www.tumblr.com/widgets/share/tool)

The Broadly Reconfigurable and Expandable Automation Device
(BREAD) is a modular data acquisition system that aims to be more
affordable than other open source alternatives. This device consists
of a backplane—referred to as a “loaf”—and various smaller PCBs—
referred to as “slices”—that interface with the loaf. The Open Science
Framework (OSF) repository for the original BREAD project is linked
towards this report’s end and holds the files and documentation for
eight different slices.

Recent Posts
Pick and Place
(https://oshe.io/post/8713
/pick-and-place/) (https://oshe.io/post/8713/pick-and-place/)
Lucas Nolen’s Work Log
(https://oshe.io/post/8959
/lucas-nolens-work-log/) (https://oshe.io/post/8959/lucas-nolens-work-log/)
Lucas Nolen
(https://oshe.io/post/8957
/lucas-nolen/) (https://oshe.io/post/8957/lucas-nolen/)
Joshua Stewart
(https://oshe.io/post/8953
/joshua-stewart/) (https://oshe.io/post/8953/joshua-stewart/)
Joshua Stewart’s Work
(https://oshe.io/post/8951 (https://oshe.io/post/8951/joshua-stewarts-work-log/)

Specifically, the Off-Grid BREAD project allows for BREAD systems to
inexpensively be implemented in outside environments. This project
involves modifying the loaf and battery management system slice
PCBs, writing Arduino code for those boards, and designing
weatherproof enclosures for the loaves and slices. All files for the
updated boards, Arduino code, and enclosures are located in the Off-
Grid BREAD OSF receptacle, which a link to is provided near the end
of this report. Additionally, links to all of the open source resources
utilized to complete this project are included as well.

/joshua-stewarts-worklog/) (https://oshe.io/post/8951/joshua-stewarts-work-log/)

Categories
Authors
(https://oshe.io/category/authors/) (https://oshe.io/category/authors/) (255)
Work Logs
(https://oshe.io/category/authors/logs/) (https://oshe.io/category/authors/logs/) (133)
Helpful Guides
(https://oshe.io/category/helpful-guides/) (https://oshe.io/category/helpful-guides/) (2)
Project Overviews
(https://oshe.io/category/project-overviews/) (https://oshe.io/category/project-overviews/) (25)
Semester Reports
(https://oshe.io/category/semester-reports/) (https://oshe.io/category/semester-reports/) (57)
2022
(https://oshe.io/category/semester-reports/2022/) (https://oshe.io/category/semester-reports/2022/)
(13)
Fall
(https://oshe.io/category/semester-reports/2022/fall-2022/) (https://oshe.io/category/semester-reports/2022/fall-2022/)
(13)
2023
(https://oshe.io/category/semester-reports/2023/) (https://oshe.io/category/semester-reports/2023/)
(30)
Fall
(https://oshe.io/category/semester-reports/2023/fall-2023/) (https://oshe.io/category/semester-reports/2023/fall-2023/)
(14)
Spring
(https://oshe.io/category/semester-reports/2023/spring-2023/) (https://oshe.io/category/semester-reports/2023/spring-2023/) (16)
2024
(https://oshe.io/category/semester-reports/2024/) (https://oshe.io/category/semester-reports/2024/)
(15)
Spring
(https://oshe.io/category/semester-reports/2024/spring/) (https://oshe.io/category/semester-reports/2024/spring/) (12) Uncategorized
(https://oshe.io/category/ (https://oshe.io/category/uncategorized/)

Goals for the project were categorized as either functional requirements or value-added, with the former being prioritized over the latter.

Functional Requirements:

1. The entire device will have design files originated entirely from free and open source software.
2. All 3D printed components can be produced by an unmodified Ender 3.
3. The battery management system slice shall be able to be powered from either a motor or a solar panel.
4. A power management slice library shall exist to allow control of the BMS and charge circuitry.
5. A physical enclosure for the outdoors shall protect the circuitry from spray and the elements.
6. A benchtop enclosure shall hold the LOAF and allow for easy storage and mounting around the lab.
7. A standard enclosure for slices shall hold slices individually.

Value-Added Goals:

1. The power management slice shall be able to be powered by a motor and a solar panel simultaneously.
2. An Arduino Library shall exist to allow the LOAF to record data to the onboard SD card.
3. All peripheral ports are accessible with the enclosure in place.
4. A four-slice LOAF shall be designed for smaller footprint applications.
5. A physical enclosure for the four-slice LOAF shall be printed.

BMS Programs

The BMS program is written in arduino and it contains the instructions to control the Battery Management Slice. This code handles pin assignments, charging voltage and current monitoring as well as communication to allow logging to the micro SD card on the BREAD loaf. This program should be uploaded to the arduino nano on the BMS slice.

SD Receiver Program uncategorized/) (https://oshe.io/category/uncategorized/) (27)

Archives
November 2025
(https://oshe.io/post/date/2025/11/) (https://oshe.io/post/date/2025/11/) (79)
October 2025
(https://oshe.io/post/date/2025/10/) (https://oshe.io/post/date/2025/10/) (2)
February 2025
(https://oshe.io/post/date/2025/02/) (https://oshe.io/post/date/2025/02/) (2)
January 2025
(https://oshe.io/post/date/2025/01/) (https://oshe.io/post/date/2025/01/) (22)
December 2024
(https://oshe.io/post/date/2024/12/) (https://oshe.io/post/date/2024/12/) (1)
September 2024
(https://oshe.io/post/date/2024/09/) (https://oshe.io/post/date/2024/09/) (9)
August 2024
(https://oshe.io/post/date/2024/08/) (https://oshe.io/post/date/2024/08/) (52)
May 2024
(https://oshe.io/post/date/2024/05/) (https://oshe.io/post/date/2024/05/) (1)
April 2024
(https://oshe.io/post/date/2024/04/) (https://oshe.io/post/date/2024/04/) (15)
March 2024
(https://oshe.io/post/date/2024/03/) (https://oshe.io/post/date/2024/03/) (15)
January 2024
(https://oshe.io/post/date/2024/01/) (https://oshe.io/post/date/2024/01/) (26)
December 2023
(https://oshe.io/post/date/2023/12/) (https://oshe.io/post/date/2023/12/) (17)
November 2023
(https://oshe.io/post/date/2023/11/) (https://oshe.io/post/date/2023/11/) (1)
September 2023
(https://oshe.io/post/date/2023/09/) (https://oshe.io/post/date/2023/09/) (87)
April 2023
(https://oshe.io/post/date/2023/04/) (https://oshe.io/post/date/2023/04/) (15)
December 2022
(https://oshe.io/post/date (https://oshe.io/post/date/2022/12/)

The SD receiver program writes log files to the SD card on the loaf using Arduinos SD library. This is accomplished by establishing communication between the arduino on the loaf and an arduino on a slice using I2C. This program should be uploaded to the loaf’s arduino nano. If you wish to change the log file names this can be accomplished by modifying the filename variable in the program. It is also worth noting that the size of the communicated information can be changed in the program by modifying Line 45. Modifying Line 45 can also allow communication with other devices communication on I2C such as another slice.

BREAD Loaves

The previous BREAD loaf design was revised to have components now uniformly spaced to facilitate future modifications and compatibility with the BREAD box. The updates to this loaf were made in the open source electronic design automation software KiCad.

Formerly, only an eight-slice loaf design existed, so a BREAD loaf capable of holding up to four slices was designed for smaller applications. This four-slice loaf was derived from the eight-slice loaf and has identical functionality, apart from its capacity of four slices as opposed to eight. The four-slice loaf is approximately half the size of the eight-slice loaf, allowing for an alternative that is easier to store and transport—as well as less expensive to manufacture—for applications that require the concurrent use of no more than four BREAD slices.

BREAD Boxes

BREAD boxes are 3d printable designs to enclose and protect both full loaves and individual slices. The boxes are designed to be printed on an Ender3 or equivalent printer and do not require support. The FreeCAD, .STL, and .3mf files for the boxes are available on the off grid BREAD OSF.

Battery Management System (BMS) Slice

/2022/12/) (https://oshe.io/post/date/2022/12/) (13) The BMS has been redesigned to include a buck converter that will allow an additional power supply—up to 32V—to power it.
Meanwhile, the original power input still accepts up to 10V, and the
output remains at slightly below 12V. The buck converter includes an
LM2596 and reduces the up to 32V input voltage to 7V so as not to damage the BQ24074 charging chip. The 4.4V output from the BQ24074 acts as the input for the MT3608 boost converter, which raises the voltage and outputs 12V.

The redesigned BMS has the capability of being powered by a 5V source with a micro USB connector and sources connected to the power ins that accept a range of voltages with a minimum input voltage of approximately 4V. Additionally, the BMS can charge a lithium-polymer battery with a JST PH 2-pin connector. Although testing the powering and charging aspects of the new BMS proved to be successful, it is important to note that its charging indicator does not light up at the appropriate time; instead, it acts as a second power indicator—mirroring the power LED and only lighting up when the BMS is receiving power, as opposed to when the BMS is charging a battery.

This issue did not arise in the previous iteration of the BMS which did not include the buck converter and ability to accept an input power supply of up to 32V. While the functionality of the most recent BMS design is not impaired—and it now allows for a power input with a maximum input voltage more than triple that of either of the preexisting power inputs—the complication with the charging LED indicates that the BMS is not yet optimized and requires further development.

Although the specific cause of the problem with the charging indicator has not yet been identified, it most likely arises from the BQ24074 charging chip or the Arduino Nano. The BQ24074 is responsible for determining when the battery is charging and influencing the output of its ninth pin to reflect the charging status. The output voltage from the BQ24074’s pin 9 is the input for the D5 Arduino pin, and this signal is then output from the D7 pin to the charging LED. Since the voltage the charging indicator receives is

- Previous Post
Restruder
(https://oshe.io/post/902/restruder/) (https://oshe.io/post/902/restruder/)

Next Post
Open Source Ornithological Recording Device
(https://oshe.io/post/924/opensource-ornithological-recordingdevice/) (https://oshe.io/post/924/open-source-ornithological-recording-device/)

primarily determined by the BQ24074 and the Arduino Nano, it is probable that the issue with the redesigned BMS involves one or both of those components.

BMS Slice Bill of Materials

BREAD_SLC_BMS_BOM.xlsx
(https://docs.google.com/spreadsheets/d/1VQjAE8BdiWcq93kpTTma5yS9mUE5ZC3-/edit?
usp=sharing&ouid=116629335165702395560&rtpof=true&sd=true) (https://docs.google.com/spreadsheets/d/1VQjAE8BdiWcq93kpTTma5yS9mUE5ZC3-/edit?usp=sharing&ouid=116629335165702395560&rtpof=true&sd=true)
Project | OSF Link
Off-Grid BREAD | https://osf.io/98m6k/ (https://osf.io/98m6k/)
BREAD | https://osf.io/u2h4g/ (https://osf.io/u2h4g/)
Open Source Software | Link
Arduino IDE | https://www.arduino.cc/en/software (https://www.arduino.cc/en/software)
KiCad | https://www.kicad.org/ (https://www.kicad.org/)
FreeCAD | https://www.freecad.org/(https://www.freecad.org/)

## Michigan Technological University (https://www.mtu.edu/enterprise/) Open Source Hardware Enterprise (https://openhardware.eit.mtu.edu/)

Lab Located in Room 901
Dow Environmental Sciences and Engineering Building, 1400 Townsend Dr, Houghton, MI 49931

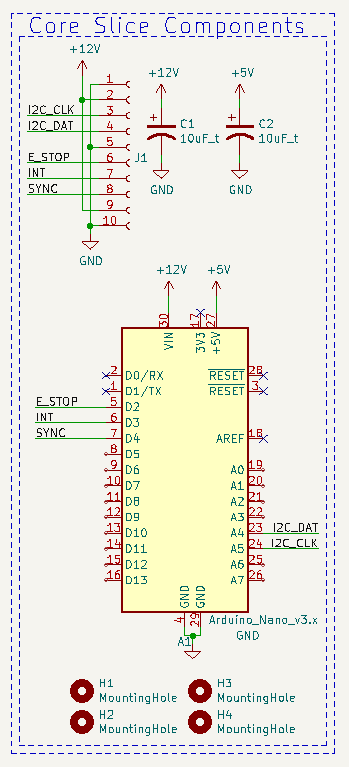
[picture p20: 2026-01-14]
BREAD CAN update/media/TemplateSchematic.png

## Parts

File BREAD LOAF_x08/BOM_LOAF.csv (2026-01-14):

Id | Designator | Package | Quantity | Designation | Supplier and ref | Cost per part | Total Cost
1 | C1, C2 | C_1206_3216Metric_Pad1.33x1.80mm_HandSolder | 2 | 10uF_t | https://www.digikey.ca/short/qfrbqfhd | $0.81 | $1.62
2 | U1 | micro_SD_LOAF | 1 | microSD_Connector | https://www.digikey.ca/en/products/detail/gct/MEM2061-01-188-00-A/9859612 | $1.74 | $1.74
3 | A1 | Arduino_Nano | 1 | Arduino_Nano_v3.x | https://www.amazon.ca/KeeYees-Module-ATmega328P-CH340G-Arduino/dp/B0816SGKHH | $9.58 | $9.58
5 | J1, J2, J3, J4, J5, J6, J7, J8 | PinHeader_1x10_P2.54mm_Vertical | 8 | Conn_01x10_Male | https://www.digikey.ca/en/products/detail/adam-tech/PH1-10-UA/9830653 | $0.25 | $2.00
6 | J11, J12 | PinHeader_1x06_P2.54mm_Vertical | 2 | Conn_01x06_Female | https://www.digikey.ca/en/products/detail/sullins-connector-solutions/PPTC061LFBN-RC/810145 | $0.72 | $1.44
7 | J9 | TerminalBlock_Phoenix_MKDS-1,5-2_1x02_P5.00mm_Horizontal | 1 | Screw_Terminal_01x02 | https://www.digikey.ca/short/q7wbhd | $0.68 | $0.68
8 | J10 | PinHeader_1x03_P2.54mm_Vertical | 1 | Conn_01x03_Male | https://www.digikey.ca/en/products/detail/adam-tech/PH1-03-UA/9830289 | $0.14 | $0.14
 |  |  |  |  |  | Total | $17.20

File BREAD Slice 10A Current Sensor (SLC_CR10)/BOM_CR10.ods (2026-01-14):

Id | Designator | Package | Quantity | Designation | Supplier and ref
1 | U4,U3,U2,U1 | SOIC-16W_7.5x10.3mm_P1.27mm | 4 | ACS723KMATR-10AB-T | https://www.mouser.ca/ProductDetail/Allegro-MicroSystems/ACS723KMATR-10AB-T?qs=pUKx8fyJudDWmsCYh0jiWw%3D%3D&mgh=1
2 | J5,J4,J3,J2 | TerminalBlock_TE_282834-2_1x02_P2.54mm_Horizontal | 4 | Screw_Terminal_01x02 | https://www.digikey.ca/en/products/detail/on-shore-technology-inc/OSTVN02A150/1588862
3 | C1,C2 | C_2312 | 2 | 10uF_t | https://www.mouser.ca/ProductDetail/Kyocera-AVX/TAJC106K016PNJ?qs=ZjRtS80k2UMUMDO3iOPrkg%3D%3D
4 | A1 | Arduino_Nano | 1 | Arduino_Nano_v3.x | https://www.digikey.ca/en/products/detail/arduino/A000005/2638989
5 | J1 | PinSocket_1x10_P2.54mm_Horizontal | 1 | Conn_01x10_Female | https://www.digikey.ca/en/products/detail/sullins-connector-solutions/PPPC101LGBN-RC/775943?s=N4IgTCBcDaIMoFYAsAOBBaAcgERAXQF8g

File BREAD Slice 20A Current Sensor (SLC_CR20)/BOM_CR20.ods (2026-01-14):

Id | Designator | Package | Quantity | Designation | Supplier and ref
1 | A1 | Arduino_Nano | 1 | Arduino_Nano_v3.x | https://www.digikey.ca/en/products/detail/arduino/A000005/2638989
2 | C1, C2 | C_2312 | 2 | 10uF_t | https://www.mouser.ca/ProductDetail/Kyocera-AVX/TAJC106K016PNJ?qs=ZjRtS80k2UMUMDO3iOPrkg%3D%3D
3 | J1 | PinSocket_1x10_P2.54mm_Horizontal | 1 | Conn_01x10_Female | https://www.digikey.ca/en/products/detail/sullins-connector-solutions/PPPC101LGBN-RC/775943?s=N4IgTCBcDaIMoFYAsAOBBaAcgERAXQF8g
4 | J2, J3, J4, J5, J6, J7, J8, J9 | Blade_Connector | 8 | Conn_01x01_Male | https://www.digikey.ca/en/products/detail/keystone-electronics/4966/303924
5 | U1, U2, U3, U4 | SOIC-16W_7.5x10.3mm_P1.27mm | 4 | ACS723KMATR-20AB-T | https://www.mouser.ca/ProductDetail/Allegro-MicroSystems/ACS723KMATR-20AB-T?qs=pUKx8fyJudAo01LNhRpkZA%3D%3D&mgh=1

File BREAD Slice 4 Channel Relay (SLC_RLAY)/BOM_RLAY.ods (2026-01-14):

Id | Designator | Package | Quantity | Designation | Supplier and ref | Cost per part | Total
1 | U2,U4,U3,U1 | SOP-4_4.4x2.6mm_P1.27mm | 4 | EL3H7 | https://www.digikey.ca/en/products/detail/everlight-electronics-co-ltd/EL3H7-B-TA-VG/2675688 | $0.47 | $1.88
2 | RV4,RV3,RV2,RV1 | Potentiometer_Bourns_3266W_Vertical | 4 | 10k | https://www.digikey.ca/en/products/detail/bourns-inc/3266W-1-103LF/1087907 | $5.59 | $22.36
3 | R4,R3,R2,R1 | R_1206_3216Metric_Pad1.30x1.75mm_HandSolder | 4 | 1k | https://www.digikey.ca/en/products/detail/stackpole-electronics-inc/RMCF1206FT1K00/1759616 | $6.21 | $24.84
4 | K4,K3,K2,K1 | Relay_SPDT_Omron-G5Q-1 | 4 | G5Q-1 | https://www.digikey.ca/en/products/detail/omron-electronics-inc-emc-div/G5Q-1-DC5/1815726?productid= | $1.66 | $6.64
5 | J6 | TerminalBlock_TE_282834-4_1x04_P2.54mm_Horizontal | 1 | Screw_Terminal_01x04 | https://www.digikey.ca/en/products/detail/on-shore-technology-inc/OSTVN04A150/1588864 | $2.01 | $2.01
6 | J5,J4,J3,J2 | TerminalBlock_TE_282834-3_1x03_P2.54mm_Horizontal | 4 | Screw_Terminal_01x03 | https://www.digikey.ca/en/products/detail/on-shore-technology-inc/OSTVN03A150/1588863 | $1.51 | $6.04
7 | D8,D7,D6,D5 | D_1206_3216Metric_Pad1.42x1.75mm_HandSolder | 4 | D_Zener | https://www.digikey.ca/en/products/detail/diodes-incorporated/BZT52C15-7-F/755469 | $0.32 | $1.28
8 | D4,D3,D2,D1 | D_1206_3216Metric_Pad1.42x1.75mm_HandSolder | 4 | D | https://www.digikey.ca/en/products/detail/kyocera-avx/SD1206S020S1R0/3749491 | $0.60 | $2.40
9 | C2,C1 | C_2312 | 2 | 10uF_t | https://www.digikey.ca/short/qfrbqfhd | $0.81 | $1.62
12 | A1 | Arduino_Nano | 1 | Arduino_Nano_v3.x | https://www.digikey.ca/en/products/detail/arduino/A000005/2638989 | $9.58 | $9.58
13 | J1 | PinSocket_1x10_P2.54mm_Horizontal | 1 | Conn_01x10_Female | https://www.digikey.ca/en/products/detail/sullins-connector-solutions/PPPC101LGBN-RC/775943?s=N4IgTCBcDaIMoFYAsAOBBaAcgERAXQF8g | $1.10 | $1.10
 |  |  |  |  |  | Total | $79.75

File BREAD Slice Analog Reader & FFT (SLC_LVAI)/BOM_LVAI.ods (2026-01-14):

Id | Designator | Package | Quantity | Designation | Supplier and ref
1 | A1 | Arduino_Nano | 1 | Arduino_Nano_v3.x | https://www.digikey.ca/en/products/detail/arduino/A000005/2638989
2 | C1, C2 | C_2312 | 2 | 10uF | https://www.digikey.ca/short/qfrbqfhd
3 | C3, C4, C5, C6, C7, C8, C9, C10, C11, C12, C13, C14 | C_1206_HandSoldering | 12 | 1uF | https://www.digikey.ca/en/products/detail/samsung-electro-mechanics/CL10A105KA8NNNC/3886760
4 | J1 | PinSocket_1x10_P2.54mm_Horizontal | 1 | Conn_01x10_Female | https://www.digikey.ca/en/products/detail/sullins-connector-solutions/PPPC101LGBN-RC/775943?s=N4IgTCBcDaIMoFYAsAOBBaAcgERAXQF8g
5 | J2, J3, J4, J5 | TerminalBlock_Pheonix_MKDS1.5-2pol | 4 | Term_2 | https://www.digikey.ca/short/q7wbhd
6 | R1, R2, R3, R4, R5, R6, R7, R8, R9, R10, R11, R12, R13, R14, R15, R16, R17, R18, R19, R20, R21, R22, R23, R24, R25, R26, R27, R28, R29, R30, R31, R32, R33, R34, R35, R36, R37, R38, R39, R40, R41, R42 | R_1206_HandSoldering | 42 | 1k | https://www.digikey.ca/en/products/detail/stackpole-electronics-inc/RMCF1206FT1K00/1759616
7 | RV1, RV2, RV3, RV4, RV5, RV6, RV7, RV8, RV9, RV10, RV11, RV12 | Potentiometer_Bourns_3266W_Vertical | 12 | 10k | https://www.digikey.ca/en/products/detail/bourns-inc/3296W-1-103RLF/2535867
8 | U1, U2, U3, U4, U5, U6 | DIP-14_W7.62mm_Socket_LongPads | 6 | MCP6004 | https://www.digikey.ca/en/products/detail/microchip-technology/MCP6004-I-P/523060

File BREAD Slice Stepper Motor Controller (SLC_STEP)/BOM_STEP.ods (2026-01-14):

Id | Designator | Package | Quantity | Designation | Supplier and ref
1 | J5 | PinSocket_1x03_P2.54mm_Vertical | 1 | Conn_01x03_Male | https://www.digikey.ca/en/products/detail/sullins-connector-solutions/PREC003SAAN-RC/2774851
2 | C3,C1,C2 | C_2312 | 3 | 10uF_t | https://www.digikey.ca/short/qfrbqfhd
3 | J6 | TerminalBlock_TE_282834-2_1x02_P2.54mm_Horizontal | 1 | Screw_Terminal_01x02 | https://www.digikey.ca/en/products/detail/on-shore-technology-inc/OSTVN02A150/1588862
4 | R4,R3,R2,R1 | R_1206_3216Metric_Pad1.30x1.75mm_HandSolder | 4 | 1k | https://www.digikey.ca/en/products/detail/stackpole-electronics-inc/RMCF1206FT1K00/1759616
5 | J4,J3 | TerminalBlock_TE_282834-8_1x08_P2.54mm_Horizontal | 2 | Screw_Terminal_01x08 | https://www.digikey.ca/en/products/detail/on-shore-technology-inc/OSTVN08A150/1588868
6 | J2 | TerminalBlock_TE_282834-4_1x04_P2.54mm_Horizontal | 1 | Screw_Terminal_01x04 | https://www.digikey.ca/short/tv7tzq1r
7 | A4,A3,A2,A1 | Pololu_Breakout-16_15.2x20.3mm | 4 | Pololu_Breakout_A4988 | https://www.pololu.com/product/1182
8 | G1 | Arduino_Nano | 1 | Arduino_Nano_v3.x | https://www.digikey.ca/en/products/detail/arduino/A000005/2638989
9 | J1 | PinSocket_1x10_P2.54mm_Horizontal | 1 | Conn_01x10_Female | https://www.digikey.ca/en/products/detail/sullins-connector-solutions/PPPC101LGBN-RC/775943?s=N4IgTCBcDaIMoFYAsAOBBaAcgERAXQF8g

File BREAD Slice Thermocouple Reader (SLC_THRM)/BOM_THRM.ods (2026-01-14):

Id | Designator | Package | Quantity | Designation | Supplier and ref
1 | R5,R4,R3,R2,R1 | R_1206_3216Metric_Pad1.30x1.75mm_HandSolder | 5 | 10k | https://www.digikey.ca/en/products/detail/stackpole-electronics-inc/RNCP1206FTD10K0/2240370
2 | U4,U3,U2,U1 | SOIC-8_3.9x4.9mm_P1.27mm | 4 | MAX6675ISA+ | https://www.digikey.ca/en/products/detail/maxim-integrated/MAX6675ISA/1513517
3 | J5,J4,J3,J2 | TerminalBlock_TE_282834-2_1x02_P2.54mm_Horizontal | 4 | Screw_Terminal_01x02 | https://www.digikey.ca/en/products/detail/on-shore-technology-inc/OSTVN02A150/1588862
4 | FB8,FB7,FB6,FB5,FB4,FB3,FB2,FB1 | R_1206_3216Metric_Pad1.30x1.75mm_HandSolder | 8 | Ferrite_Bead_Small (80 ohm) | https://www.digikey.ca/en/products/detail/w%C3%BCrth-elektronik/74279215/1639033
5 | C6,C5,C4,C3 | C_1206_3216Metric_Pad1.33x1.80mm_HandSolder | 4 | 0.01 uF | https://www.digikey.ca/en/products/detail/walsin-technology-corporation/1206B103J500CT/9355096
6 | C2,C1 | C_2312 | 2 | 10uF | https://www.digikey.ca/en/products/detail/yageo/cc1206kkx5r8bb106/2833631
9 | A1 | Arduino_Nano | 1 | Arduino_Nano_v3.x | https://www.digikey.ca/en/products/detail/arduino/A000005/2638989
10 | J1 | PinSocket_1x10_P2.54mm_Horizontal | 1 | Conn_01x10_Female | https://www.digikey.ca/en/products/detail/sullins-connector-solutions/PPPC101LGBN-RC/775943?s=N4IgTCBcDaIMoFYAsAOBBaAcgERAXQF8g

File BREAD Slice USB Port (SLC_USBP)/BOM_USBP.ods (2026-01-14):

Id | Designator | Package | Quantity | Designation | Supplier and ref | Cost per part | Total
1 | J3,J2 | USB_A_Molex_67643_Horizontal | 2 | USB_A | https://www.digikey.ca/en/products/detail/molex/0676430910/917619 | $2.53 | $5.06
2 | C1,C2 | C_2312 | 2 | 10uF_t | https://www.digikey.ca/short/qfrbqfhd | $0.81 | $1.62
3 | A1 | Arduino_Nano | 1 | Arduino_Nano_v3.x | https://www.amazon.ca/KeeYees-Module-ATmega328P-CH340G-Arduino/dp/B0816SGKHH | $9.58 | $9.58
4 | J1 | PinSocket_1x10_P2.54mm_Horizontal | 1 | Conn_01x10_Female | https://www.digikey.ca/en/products/detail/sullins-connector-solutions/PPPC101LGBN-RC/775943?s=N4IgTCBcDaIMoFYAsAOBBaAcgERAXQF8g | $1.10 | $1.10
5 | U1 | MSOP-10_3x3mm_P0.5mm | 1 | FSUSB42MUX | https://www.digikey.ca/en/products/detail/onsemi/FSUSB42MUX/2036916 | $1.46 | $1.46
6 | U2 | SSOP-28_5.3x10.2mm_P0.65mm | 1 | FT232RL | https://www.digikey.ca/en/products/detail/ftdi-future-technology-devices-international-ltd/FT232RL-REEL/1836385?productid= | $6.95 | $6.95
 |  |  |  |  |  | Total | $25.77

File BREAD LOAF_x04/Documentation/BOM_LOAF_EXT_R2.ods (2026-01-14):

References | Value | Footprint | Quantity | URL
J2, J3, J4, J5 | Conn_01x10_Male | BREAD 10-Pin Connector | 4 | https://www.digikey.ca/en/products/detail/amphenol-cs-fci/10129378-910002BLF/7915958
J1 | 10129379-910002BLF | 1x10 RA Male Header 2.54mm Pitch | 1 | https://www.digikey.ca/en/products/detail/amphenol-cs-fci/10129379-910002BLF/7916010
J6 | PPPC101LGBN-RC | PinSocket_1x10_P2.54mm_Horizontal | 1 | https://www.digikey.ca/en/products/detail/sullins-connector-solutions/PPTC101LGBN-RC/775904
J7 | Barrel_Jack | BarrelJack_CUI_PJ-063AH_Horizontal | 1 | https://www.digikey.ca/en/products/detail/cui-devices/pj-063ah/2161208

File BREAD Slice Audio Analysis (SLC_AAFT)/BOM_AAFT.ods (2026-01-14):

Id | Designator | Package | Quantity | Designation | Supplier and ref
1 | U2,U1 | DIP-14_W7.62mm_SMDSocket_SmallPads | 2 | MCP6004 | https://www.digikey.ca/en/products/detail/microchip-technology/MCP6004-I-P/523060
2 | J2 | Jack_3.5mm_CUI_SJ1-3533NG_Horizontal | 1 | Aux | https://www.digikey.ca/en/products/detail/cui-devices/SJ1-3533NG/738701?productid=738701
3 | RV4,RV3,RV2,RV1 | Potentiometer_Bourns_3266W_Vertical | 4 | 10k | https://www.digikey.ca/en/products/detail/bourns-inc/3296W-1-103RLF/2535867
4 | R26 | R_1206_3216Metric_Pad1.30x1.75mm_HandSolder | 1 | 360 | https://www.digikey.ca/en/products/detail/stackpole-electronics-inc/RMCF1206JT360R/1753824
5 | R25,R24 | R_1206_3216Metric_Pad1.30x1.75mm_HandSolder | 2 | 450 | https://www.digikey.ca/en/products/detail/stackpole-electronics-inc/RMCF1206FT453R/1759215
6 | R23,R22 | R_1206_3216Metric_Pad1.30x1.75mm_HandSolder | 2 | 600 | https://www.digikey.ca/en/products/detail/yageo/RC1206FR-07604RL/729038
9 | R21,R20 | R_1206_3216Metric_Pad1.30x1.75mm_HandSolder | 2 | 900 | https://www.mouser.ca/ProductDetail/YAGEO/RT1206CRE07900RL
10 | R19,R18 | R_1206_3216Metric_Pad1.30x1.75mm_HandSolder | 2 | 1.8 k | https://www.digikey.ca/en/products/detail/stackpole-electronics-inc/RMCF1206FT1K80/1758909
11 | R17 | R_1206_3216Metric_Pad1.30x1.75mm_HandSolder | 1 | 400 | https://www.digikey.ca/en/products/detail/yageo/RT1206BRD07400RL/5936956
12 | R16,R15,R14,R13 | R_1206_3216Metric_Pad1.30x1.75mm_HandSolder | 4 | 500 | https://www.digikey.ca/en/products/detail/vishay-dale/TNPU1206500RAZEN00/6615941
13 | R12,R11,R10,R9,R8,R7,R6,R5,R4,R3,R2,R1 | R_1206_3216Metric_Pad1.30x1.75mm_HandSolder | 12 | 1k | https://www.digikey.ca/en/products/detail/yageo/RC1206FR-071KL/728387
14 | J3 | Jack_6.35mm_Neutrik_NMJ6HCD2_Horizontal | 1 | Q_Inch | https://www.mouser.ca/ProductDetail/Neutrik/NMJ6HCD2?qs=ZNZTMDotSRlKYl2qFVJbQA%3D%3D
15 | C12,C11,C10,C9,C8,C7,C6,C5,C4 | C_1206_3216Metric_Pad1.33x1.80mm_HandSolder | 9 | 0.1 uF | https://www.digikey.ca/en/products/detail/samsung-electro-mechanics/CL31B104KBCNNNC/3886675
16 | C3 | C_1206_3216Metric_Pad1.33x1.80mm_HandSolder | 1 | 10 uF | https://www.digikey.ca/en/products/detail/samsung-electro-mechanics/CL31A106KAHNNNE/3886733
17 | C1,C2 | C_2312 | 2 | 10uF_t | https://www.digikey.ca/en/products/detail/samsung-electro-mechanics/CL31A106KAHNNNE/3886733
18 | A1 | Arduino_Nano | 1 | Arduino_Nano_v3.x | https://www.digikey.ca/en/products/detail/arduino/A000005/2638989
19 | J1 | PinSocket_1x10_P2.54mm_Horizontal | 1 | Conn_01x10_Female | https://www.digikey.ca/en/products/detail/sullins-connector-solutions/PPPC101LGBN-RC/775943?s=N4IgTCBcDaIMoFYAsAOBBaAcgERAXQF8g

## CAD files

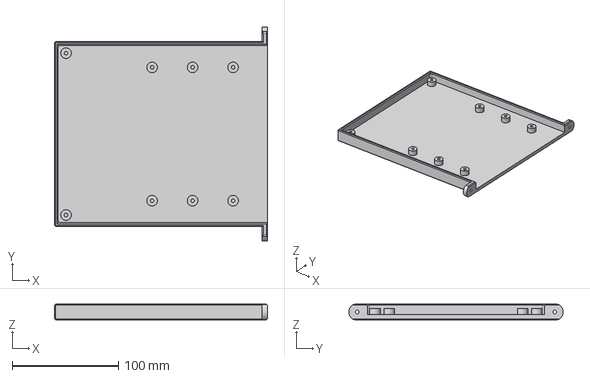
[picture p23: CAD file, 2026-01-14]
BREAD CAN update/Loaf Box pt1.step
200.5 x 201.8 x 15.0 mm

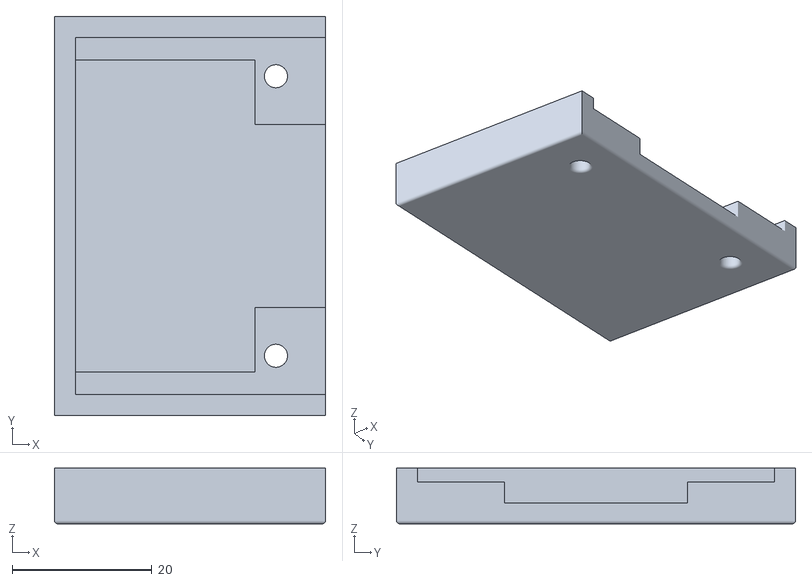
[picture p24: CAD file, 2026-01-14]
BREAD LOAF ESP32 Controller (LOAF_ESPC)/Mechanical/LOAF_ESPC Case.stl
38.8 x 57.1 x 8.00

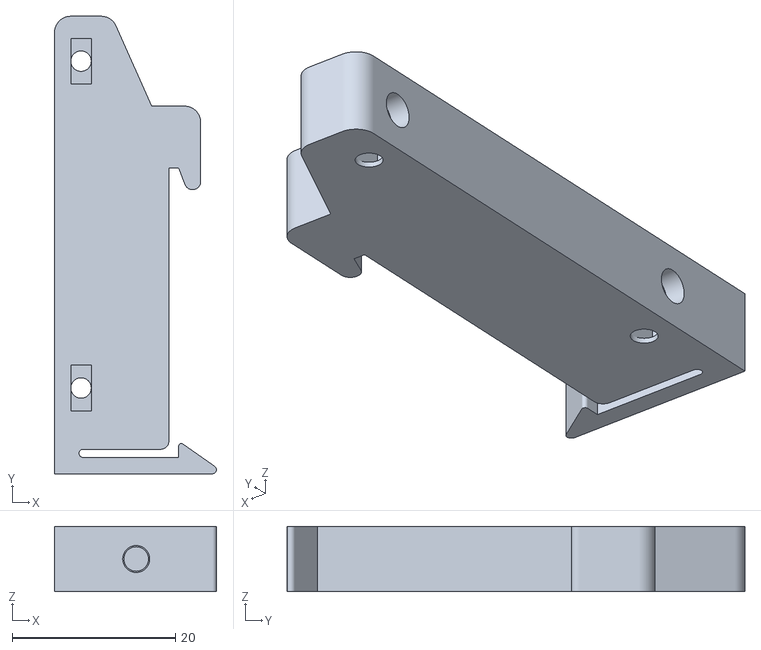
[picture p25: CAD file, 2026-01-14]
BREAD LOAF_x04/Mechanical/DIN Mount.stl
19.8 x 56.0 x 8.00

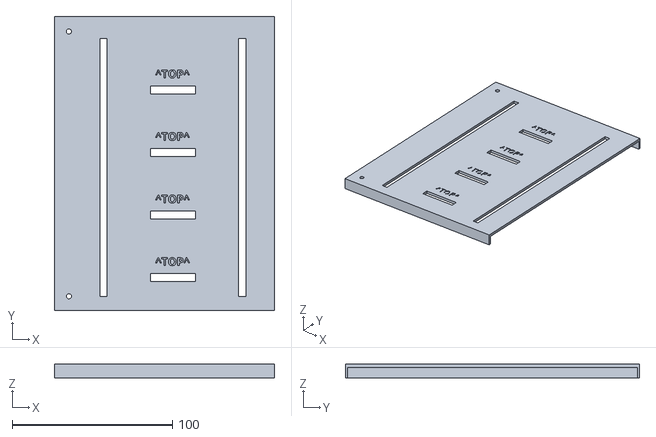
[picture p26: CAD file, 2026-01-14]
BREAD LOAF_x08/Mechanical/LOAF - Top 2.stl
137.1 x 183.5 x 8.60

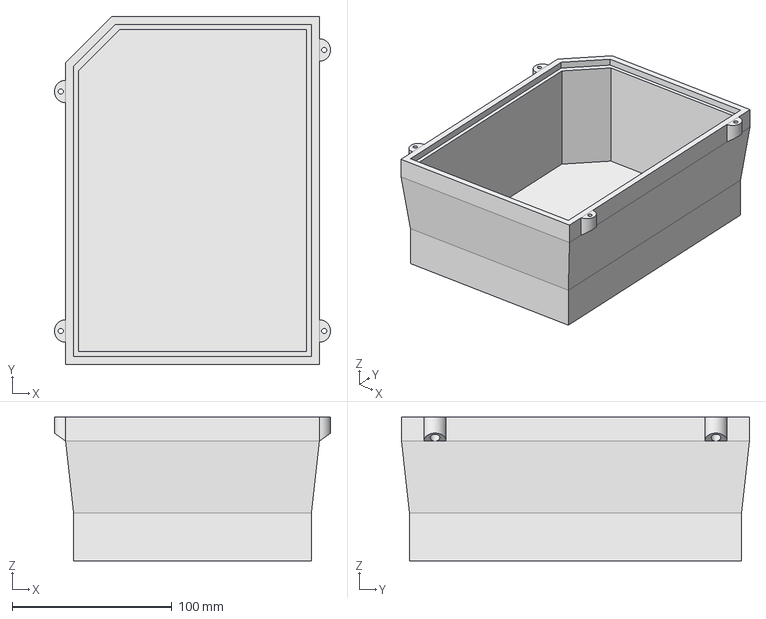
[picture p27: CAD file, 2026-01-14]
BREAD Off-Grid/BREAD 4-Slice Loaf/Mechanical Files/Half_Loaf_Top.FCStd
173.0 x 218.0 x 90.0 mm

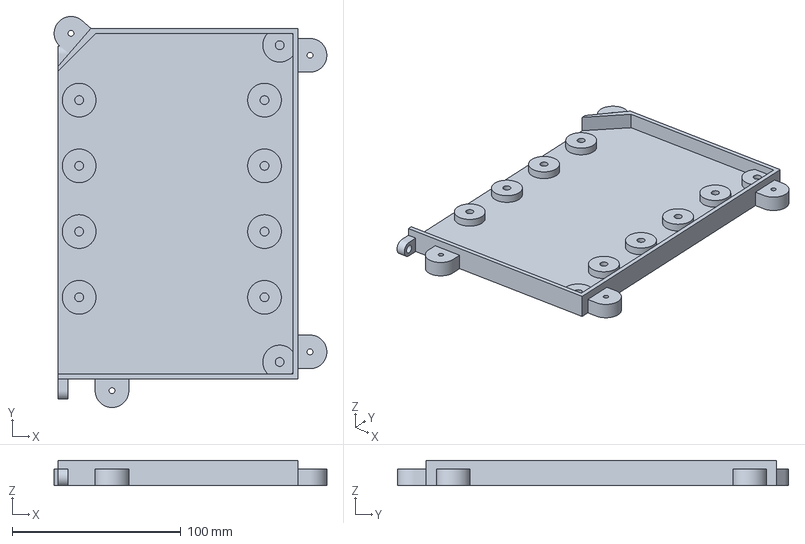
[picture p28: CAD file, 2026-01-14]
BREAD Off-Grid/BREAD 8-Slice Loaf/Mechanical Files/Right_Half_Bread_LOAF_Waterproof-Body.3mf
161.8 x 232.0 x 15.0 mm

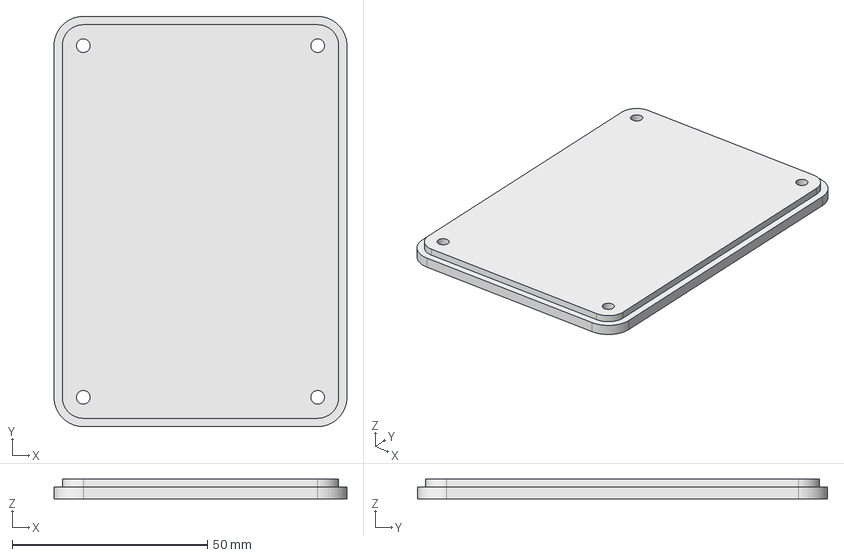
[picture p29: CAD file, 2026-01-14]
BREAD Off-Grid/BREAD Slice - Battery Management System (SLC_BMS)/Mechanical Files/Standalone_Slice_Case_Top.FCStd
75.0 x 105.0 x 5.00 mm

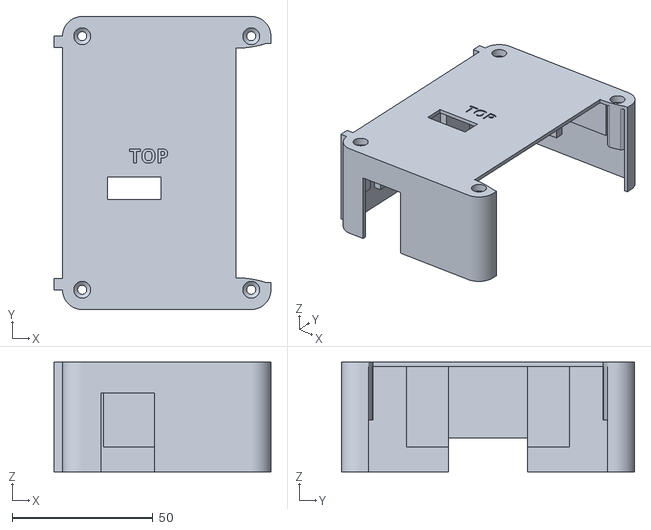
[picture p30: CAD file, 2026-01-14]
BREAD Slice 10A Current Sensor (SLC_CR10)/Mechanical/Top Case.stl
77.0 x 104.0 x 39.0

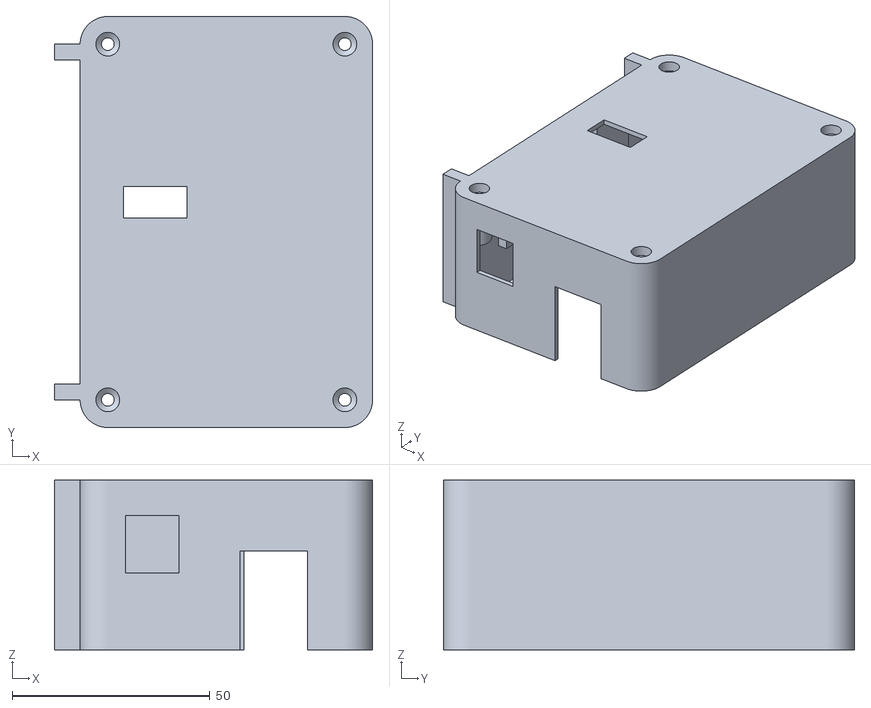
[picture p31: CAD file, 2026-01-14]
BREAD Slice Bioreactor (SPECIALIZED) (SLC_PHDO)/Mechanical/PHDO - Top.stl
80.5 x 104.0 x 43.0

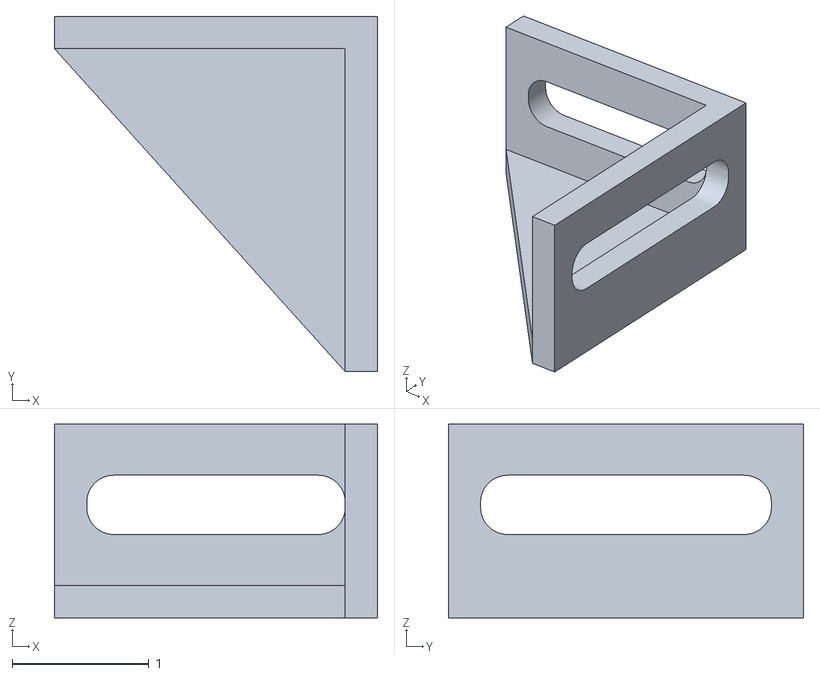
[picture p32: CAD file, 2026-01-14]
BREAD Slice BUNS/Scanner Bracket.stl
2.36 x 2.60 x 1.42

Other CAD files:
BREAD Slice DC Motor Controller (SLC_DCMT)/Mechanical/Top.stl
BREAD Slice Relay Heating Element Controller (SLC_RLHT)/Mechanical/Top.stl
BREAD CAN update/CAN Loaf Box_.step
BREAD CAN update/Loaf Box pt2.step
BREAD LOAF_x04/Mechanical/Pin Aligner.stl
BREAD LOAF_x08/Mechanical/LOAF - Base 1.stl
BREAD LOAF_x08/Mechanical/LOAF - Base 2.stl
BREAD LOAF_x08/Mechanical/LOAF - Top 1.stl
BREAD Off-Grid/BREAD 4-Slice Loaf/Mechanical Files/Half_Bread_LOAF-Body.3mf
BREAD Off-Grid/BREAD 4-Slice Loaf/Mechanical Files/Half_Bread_LOAF-Body.stl
BREAD Off-Grid/BREAD 4-Slice Loaf/Mechanical Files/Half_Bread_LOAF.FCStd
BREAD Off-Grid/BREAD 4-Slice Loaf/Mechanical Files/Half_Bread_LOAF_Waterproof-Body.3mf
BREAD Off-Grid/BREAD 4-Slice Loaf/Mechanical Files/Half_Bread_LOAF_Waterproof-Body.stl
BREAD Off-Grid/BREAD 4-Slice Loaf/Mechanical Files/Half_Bread_LOAF_Waterproof.FCStd
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

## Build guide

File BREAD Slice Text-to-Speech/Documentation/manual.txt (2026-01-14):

-------------------------------------------------------------------
SLC_TTS Manual

Broadly Reconfigurable and Expandable Automation Device (BREAD)
Text-to-Speech Slice (SLC-TTS)
-------------------------------------------------------------------

Author: Ian Huff
Date Updated: 4/12/2023
Revision 0

-- Required Materials --

- SLC_TTS PCB
- Arduino Nano
- Raspberry Pi or Raspberry Pi compatible device, connected to the Internet
- MicroSD card (size depends on your device, 8GB is a safe bet)
- Adafruit Level Shifter
- Adafruit I2S Amp
- Raspberry Pi GPIO ribbon cable
- Male & female header pins
- Soldering equipment
- USB-Mini cable
- Ethernet cable (optional, used to ssh into the Raspberry Pi)
- Computer with MicroSD reader
- Speaker

This guide will assume the computer is running Windows 11, though the steps should be similar for other operating systems.
See the Bill of Materials in the datasheet for a full list of specific pins and quantities

-- Soldering --

Note: All header pins should stand out from the front of the board (the side with the Open Source Hardware logo and board info); the solder should be applied on the back of the board.
Solder 90-degree female header pins to J1.
Solder standard female header pins to A1, U1, and U2.
Solder standard male header pins to J2.

If the Arduino Nano, level shifter, and I2S amp are not already soldered, solder their male header pins now.

-- Conections --

Insert the Arduino Nano into the female header pin slots on A1, with the USB-Mini port facing the edge of the board.
Insert the level shifter into the female header pin slots on U1, with the HV/LV and GND pins aligned with the text printed on the board.
Insert the I2S amp into the female header pin slots on U2, with the Vin, GND, DIN, BCLK, and LRC pins aligned with the text printed on the board.
Use the Raspberry Pi GPIO ribbon cable to connect the male header pins on J2 to the Raspberry Pi.
Ensure that pin 1, denoted by the square solder pad and break in the printed outline on the slice board, is correctly connected to pin 1 on the Raspberry Pi.
Connect a speaker to the terminal on the I2S amp.

-- Arduino Setup --

Plug the Arduino Nano, connected to the slice, into your computer with a USB-Mini cable.
Download and install the Arduino IDE here:
https://www.arduino.cc/en/software
Open the Arduino sketch (Firmware/SLC_TTS/SLC_TTS.ino) in the Arduino IDE.
Upload the sketch to the board by clicking the "Upload" button near the top of the window (Right Arrow icon).
When the message "Done uploading." is displayed above the console at the bottom of the window, the Arduino IDE can be closed.

If you're having trouble uploading the code to the Arduino, check Tools > Port and ensure that the correct USB port is selected.
If the issue still occurs, try using a different USB port.

-- MicroSD Card Setup --

Download and install the Raspberry Pi Imager tool here:
https://www.raspberrypi.com/software/
Insert the MicroSD card into your computer and launch the tool.
In the tool, under Operating System, select Raspberry Pi OS (other) > Raspberry Pi OS Lite
If there are multiple options available, select the Raspberry Pi OS Lite option that is most compatible with your Raspberry Pi device.
In the tool, under Storage, select the MicroSD card.

If you will be setting up the Raspberry Pi headlessly (i.e. without a monitor), click the Settings button.
Make sure the the "Set username and password" box is checked.
Set a username and passowrd. This guide will use the former defaults of "pi" for the username, and "raspberry" for the password.
Optionally, if you wish to enable ssh, make sure the "Enable SSH" box is checked.
Click the "Write" button.

The writing process tends to be prone to errors and failures, so monitor the process.
If the process fails, you may need to restart your computer before trying again.
When the process is successful, you may close the Raspberry Pi Imager.

Copy the SLC_TTS/Firmware/SLC_TTS.py file to the root of the MicroSD card.
Eject the MicroSD card from your computer, insert it into the Raspberry Pi.
If you are using an Ethernet cable to ssh into the Raspberry Pi, plug it in now.
Plug the USB-Mini cable back into the Arduino Nano to power both devices.

When the device has booted, you may be prompted to log in.
Log in using the password you set previously, or create a username and password if prompted.

-- Enabling SPI --

When using ssh over Ethernet, you can connect to the Raspberry Pi with the command "ssh pi@raspberrypi.local"
The device may take some time to boot.

If a message is displayed indicating that the remote host identification has changed:
Navigate to the file C://Users/[username]/.ssh/known_hosts.
Open the file using Notepad or another text editor and delete and lines beginning with "raspberrypi.local"
Save the file and try the ssh again.

Once you have logged in to the device, run the command "sudo raspi-config"
This will display a menu with several configuration options.
Navigate to option 3, "Interface Options", and press Enter.
Navigate to option I4, "SPI", and press Enter.
A window will be displayed which asks "Would you like the SPI interface to be enabled?"
Select "<Yes>"
On success, the message "The SPI interface is enabled" will be displayed.
Selecting "<Ok>" will return you to the main config window.
Select "<Finish>" to return to the terminal.

-- Enabling I2S --

Instructions on how to enable the I2S interface for GPIO audio can be found at the following website:
https://learn.adafruit.com/adafruit-max98357-i2s-class-d-mono-amp/raspberry-pi-usage

You may find that the default keyboard layout does not match your keyboard.
If this is the case, you can change the keyboard layout by running "sudo raspi-config" and navigating to Localisation Options.

-- Installing eSpeak --

Run the command "sudo apt-get install espeak". The Raspberry Pi will need to be connected to the Internet.
If prompted to confirm, say yes.

-- Enabling auto-boot --

------- WIP - THIS METHOD IS NOT CONSISTENT -------

Enter the command "sudo crontab -e".
If prompted to select an editor, select nano (most likely option 1).
When the text editor has loaded, add the following line to the end of the file:

@reboot sleep 60 python3 /boot/SLC_TTS.py

The "sleep 60" adds a 60 second delay before the script starts, ensuring that the SPI interface is activated correctly.
To save the file, press Ctrl+X, then Y to confirm, then Enter to confirm.
When the device is next rebooted, it should automatically run the SLC_TTS.py script.

-- Usage Overview --

Once the board is powered, the Raspberry Pi will take some time to boot.
Once complete, serial data containing a string of text can be sent to the device's Arduino Nano.
The data will then be forwarded to the Raspberry Pi via SPI.
On receipt of a string of text, the Raspberry Pi will generate speech audio and play it.

To run the script manually, after logging in to the Raspberry Pi, run the command "python3 /boot/SLC_TTS.py"
When the Arduino Nano is powered via a USB cable connected to a computer, the Arduino IDE's Serial Monitor can be used to send text data.

Currently, there is a limit of around 60 characters, so try to keep messages short until this is remedied.

-- Special Commands --

Sending a string that begins with "###" will indicate that the string is a command
Commands will not be spoken. Instead, they allow settings to be changed.
Currently implemented commands:
  - ### volume <int>
    - Sets the espeak -a flag to <int>
	- Default: 10
	- Values lower than 10 will reduce the volume, and vice versa.

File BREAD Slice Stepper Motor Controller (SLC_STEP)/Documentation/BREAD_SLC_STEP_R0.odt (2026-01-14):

# Broadly Reconfigurable and Expandable Automation Device (BREAD) – Slice Datasheet: Stepper Motor Control Slice (SLC-STEP)

By: Nicholas Whisman (ngwhisma@mtu.edu) – Revision 0, on 18. May 2021

## Short Device Description

This device is designed to very finely control up to four stepper motors. The system has a feedback path in the form of 4 analog inputs. Finer control can be achieved by utilizing the microstep pin connections.

## Quick Information

Device at a Glance

Short title | Stepper Motor Control Slice
Part # | SLC-STEP
Repository Link | Link to OSF or other repository
Academic Paper DOI | DOI link to published paper
Device Cost | Monetary cost of the device
Assembly Difficulty | Difficult, Millable
Application Area | Controls, Robotics

Device Connections

J2 – Analog Input Paths

Pin # | Description | Rating
1 | Analog Input 1 | 5V
2 | Analog Input 2 | 5V
3 | Analog Input 3 | 5V
4 | Analog Input 4 | 5V

J3 – Output to Stepper

Pin # | Description | Rating
1 | Motor 2, Signal 1B | ±2A
2 | Motor 2, Signal 1A | ±2A
3 | Motor 2, Signal 2A | ±2A
4 | Motor 2, Signal 2B | ±2A
5 | Motor 1, Signal 1B | ±2A
6 | Motor 1, Signal 1A | ±2A
7 | Motor 1, Signal 2A | ±2A
8 | Motor 1, Signal 2B | ±2A

J4 – Output to Stepper

Pin # | Description | Rating
1 | Motor 3, Signal 2B | ±2A
2 | Motor 3, Signal 2A | ±2A
3 | Motor 3, Signal 1A | ±2A
4 | Motor 3, Signal 1B | ±2A
5 | Motor 4, Signal 2B | ±2A
6 | Motor 4, Signal 2A | ±2A
7 | Motor 4, Signal 1A | ±2A
8 | Motor 4, Signal 1B | ±2A

## Commands

Set Up (no significant returns)
Byte: Address | Bit: 1 | Float: Target Temp | Float: Ramp Rate (d/m)
Speed Select (no significant returns)
Byte: Address | Bit: 0 | Float: 0 | Float: 0
Step Select (no significant returns)
Analog Read (returns voltage on selected analog input line)

## Schematic

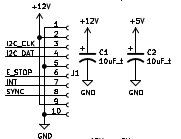
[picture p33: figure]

Figure 1: BREAD Connection Port and Power Capacitors

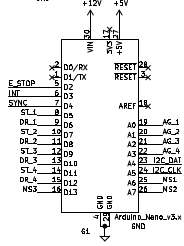
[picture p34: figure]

Figure 2: Arduino Nano

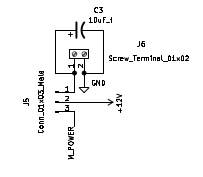
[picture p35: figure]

Figure 3: Custom Power Select

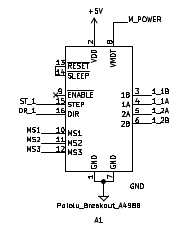
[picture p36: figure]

Figure 4: One of four breakout stepper motor drivers

Figure 5: One of four feedback voltage paths

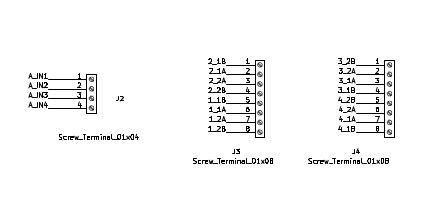
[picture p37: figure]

Figure 6: Signal Input Ports

## Bill of Materials

Designator | Description | Quantity | Cost / part | URL
J5 | 01x03 1/10” Pitch Male Connector Pins | 1 | 0.27 | https://www.digikey.com/short/jv0b95z0
C1-3 | 1206 Packaging 10 µF Capacitor | 3 | 0.64 | https://www.digikey.com/short/qfrbqfhd
J6 | 01x02 1/10” Pitch Terminal Block | 1 | 1.27 | https://www.digikey.com/short/0v8hf4h8
R1-4 | 1k 1206 Packaging Resistor | 4 | 0.10 | https://www.digikey.com/short/wp8502p7
J3-4 | 01x08 1/10” Pitch Terminal Block | 2 | 6.45 | https://www.digikey.com/short/mqn9fd88
J2 | 01x04 1/10” Pitch Terminal Block | 1 | 2.75 | https://www.digikey.com/short/tv7tzq1r
D1-4 | 5.1V Zener Diode | 4 | 0.22 | https://www.digikey.com/short/z0f0ztp2
A1-4 | Pololu A4988 Stepper Driver | 4 | 5.95 | https://www.pololu.com/category/156/a4988-stepper-motor-driver-carriers
G1 | Arduino Nano | 1 | 22.00 | https://www.digikey.com/en/products/detail/arduino/A000005/2638989
J1 | 01x10 Female Header Pins | 1 | 0.79 | https://www.digikey.com/short/23bfwwjh

## Construction & Fabrication

List any tools that are required and short guide on the order which parts should be soldered / assembled. Be sure to note any specialized methods and point out components that may easily be soldered in the incorrect orientation. Additionally include at least one picture of the assembled board (include both sides if there are components on both sides).

[Image of the assembled Circuit Board]

Fig #. Subtitle should go here.

## Configuration & Calibration

Include a list of default jumper and potentiometer positions:

Hardware Positions

- Turn P1 to be roughly 50%
- Turn P2 to be completely closed (turn clockwise until potentiometer clicks)
- Place a jumper to short out J3. Etc…

Detail any key parameters the end-user may want to adjust in the firmware, and if there are any special instructions before programming the Slice.

Tools Required For Calibration

- An oscilloscope with at least 15Mhz sampling
- A multimeter. Etc…

List all of the tools / instruments required for calibration. Provide a detailed & step by step guide on how to calibrate (or validate) each unique type of channel on the card. Include what variables in the firmware may need to be adjusted (and when). Attach a wiring diagram for each relevant calibration circuit.

[Image of the calibration circuit]

Fig #. Subtitle should go here.

## Usage & Constraints

List the relevant constraints for each type of channel on the card. These parameters may be quantities like max current, max voltage, frequency, sampling frequency, etc.

List an example wiring diagram of the slice in use, as well as some suggested applications

[Image of the example usage wiring diagram]

Fig #. Subtitle should go here.

## General Comments on Slice

This section is intended as a catch-all for any topics that are relevant to the Slice that don’t fit in any other category.

## Revision Notes

- Rev 0 – Initial document release (DATE HERE)

SLC-STEP Datasheet – Revision 0

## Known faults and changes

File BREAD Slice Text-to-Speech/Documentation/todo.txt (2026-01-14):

- full loaf compatibility
- more consistent auto boot
- commands
  - speed adjustment?
  - change the voice?
- option to log all outputs into a txt file

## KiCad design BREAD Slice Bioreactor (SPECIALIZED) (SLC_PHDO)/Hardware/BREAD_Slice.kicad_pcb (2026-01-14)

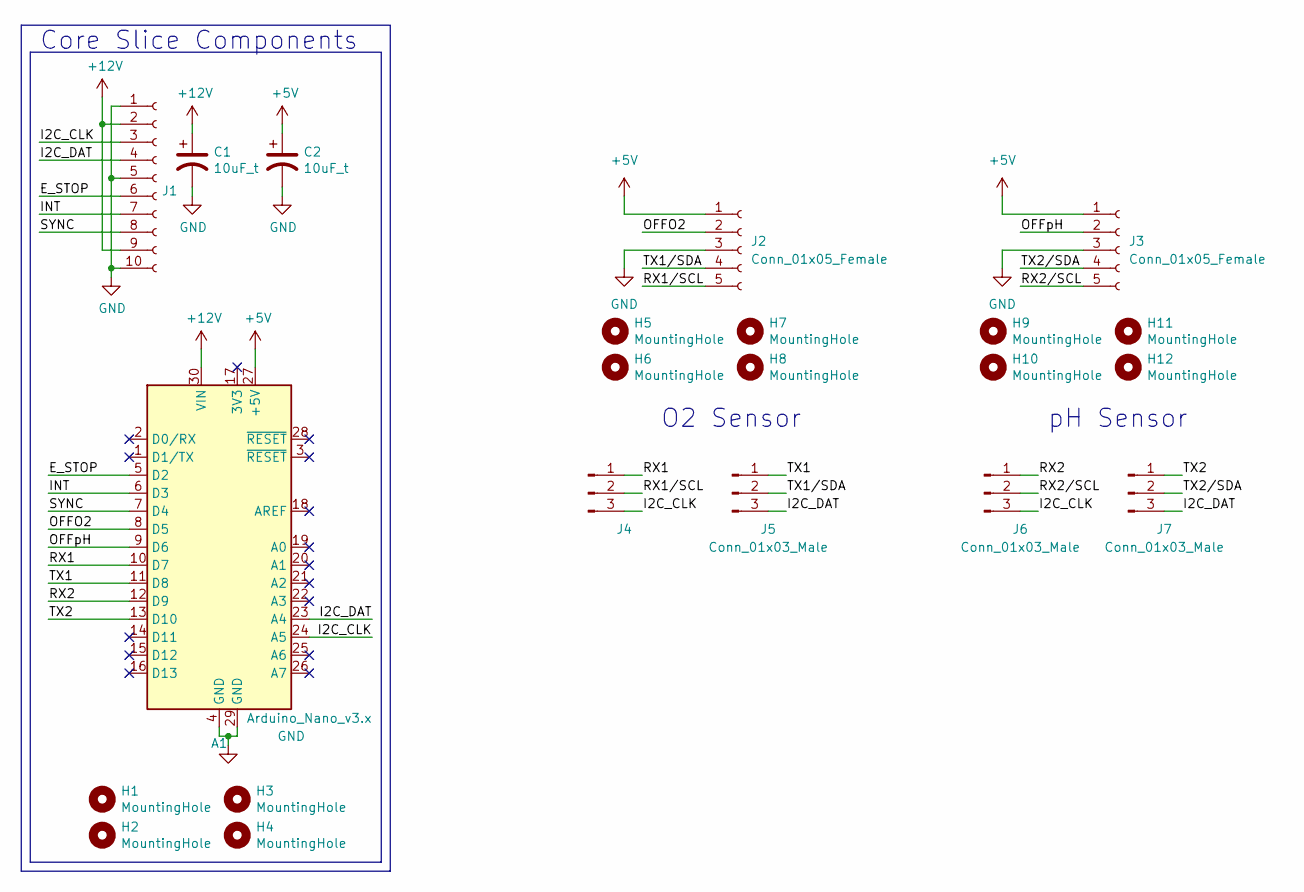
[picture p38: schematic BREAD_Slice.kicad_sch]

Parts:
A1: Arduino_Nano_v3.x; Arduino_Nano
C1, C2: 10uF_t; C_1206_3216Metric_Pad1.33x1.80mm_HandSolder; Part # T491C106K025AT
H1, H2, H3, H4, H5, H6, H7, H8, H9, H10, H11, H12: MountingHole; MountingHole_3.2mm_M3_DIN965_Pad
J1: Conn_01x10_Female; PinSocket_1x10_P2.54mm_Horizontal
J2, J3: Conn_01x05_Female; PinSocket_1x05_P2.54mm_Vertical
J4: (no value)
J5: Conn_01x03_Male
J6, J7: Conn_01x03_Male; PinSocket_1x03_P2.54mm_Vertical

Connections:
+5V: A1.27 (+5V), C2.1, J2.1, J3.1
+12V: A1.30 (VIN), C1.1, J1.2, J1.9
/E_STOP: A1.5 (D2), J1.6
/I2C_CLK: A1.24 (A5), J1.3, J4.3, J6.3
/I2C_DAT: A1.23 (A4), J1.4, J5.3, J7.3
/INT: A1.6 (D3), J1.7
/OFFO2: A1.8 (D5), J2.2
/OFFpH: A1.9 (D6), J3.2
/RX1: A1.10 (D7), J4.1
/RX1/SCL: J2.5, J4.2
/RX2: A1.12 (D9), J6.1
/RX2/SCL: J3.5, J6.2
/SYNC: A1.7 (D4), J1.8
/TX1: A1.11 (D8), J5.1
/TX1/SDA: J2.4, J5.2
/TX2: A1.13 (D10), J7.1
/TX2/SDA: J3.4, J7.2
GND: A1.4 (GND), A1.29 (GND), C1.2, C2.2, J1.1, J1.5, J1.10, J2.3, J3.3

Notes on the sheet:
O2 Sensor
pH Sensor
Core Slice Components

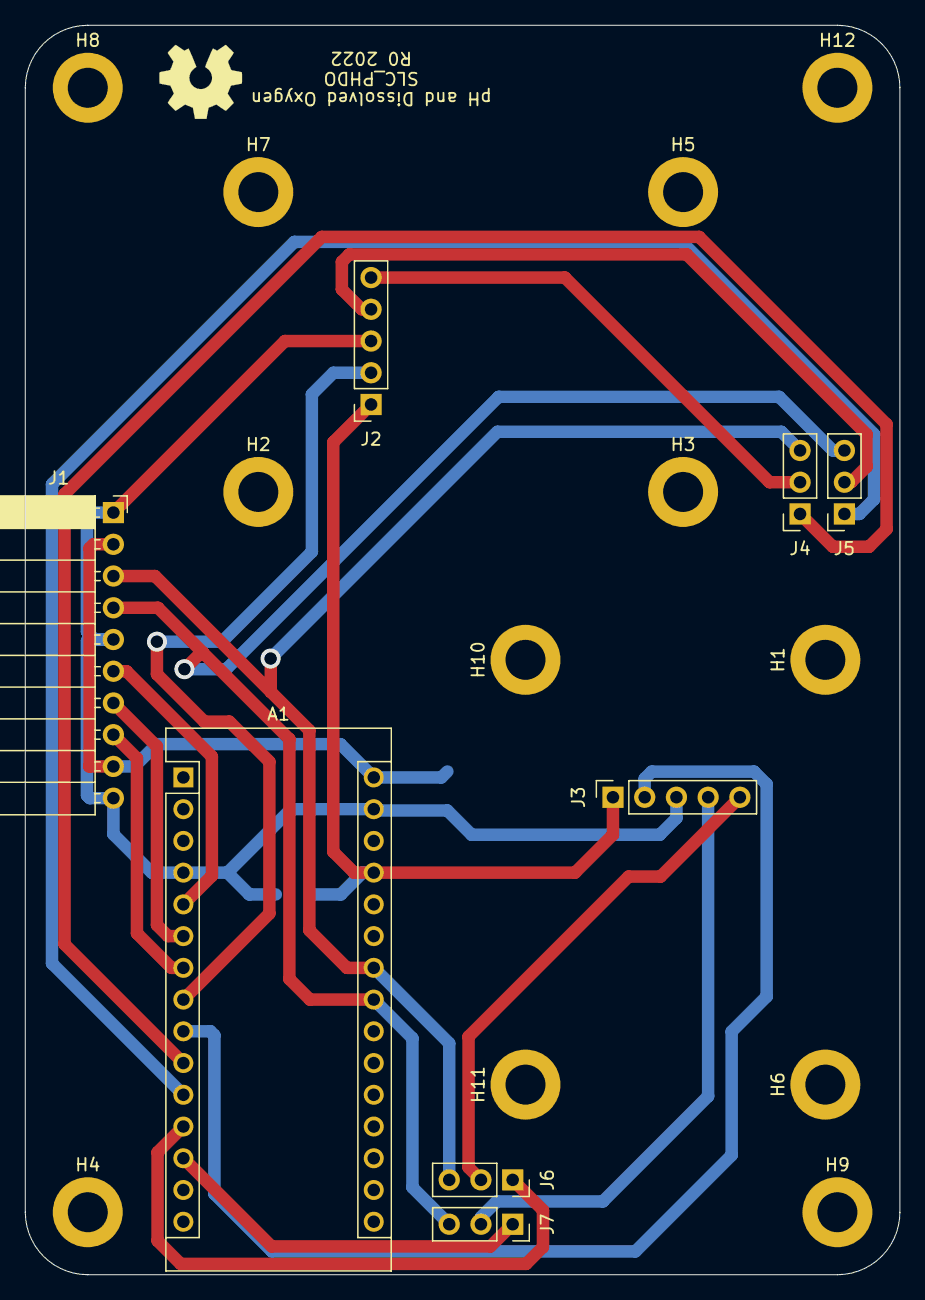
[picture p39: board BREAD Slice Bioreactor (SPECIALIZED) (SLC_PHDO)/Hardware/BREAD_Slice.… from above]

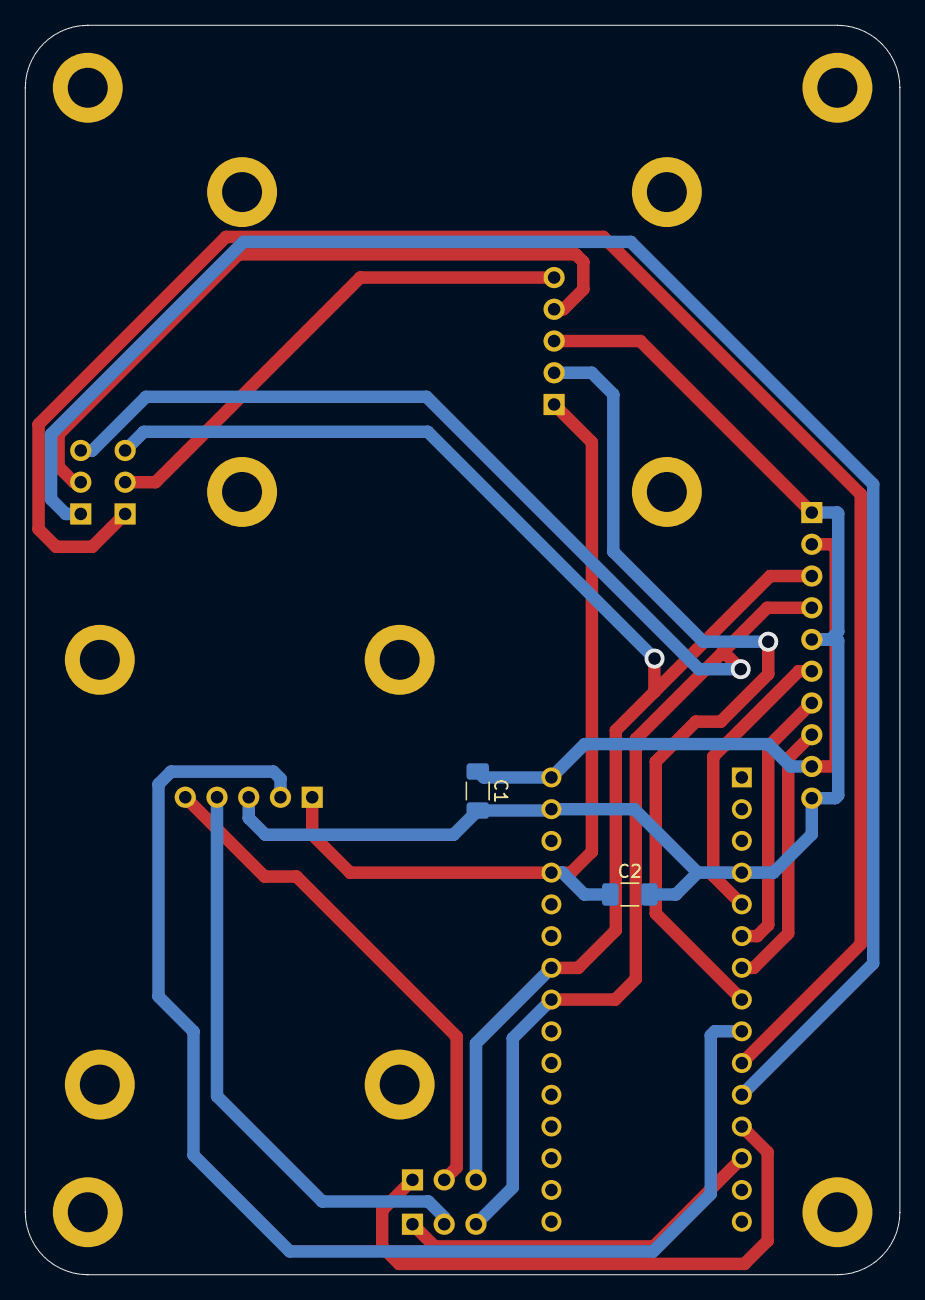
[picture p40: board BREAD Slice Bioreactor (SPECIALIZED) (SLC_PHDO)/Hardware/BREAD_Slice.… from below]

Board: 2 copper layers, 70.0 x 100.0 mm, 23 parts (2 on the bottom side), 18 nets.

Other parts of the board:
Logo1: Logo_Open_Hardware_Small; OSHW-Symbol_6.7x6mm_SilkScreen

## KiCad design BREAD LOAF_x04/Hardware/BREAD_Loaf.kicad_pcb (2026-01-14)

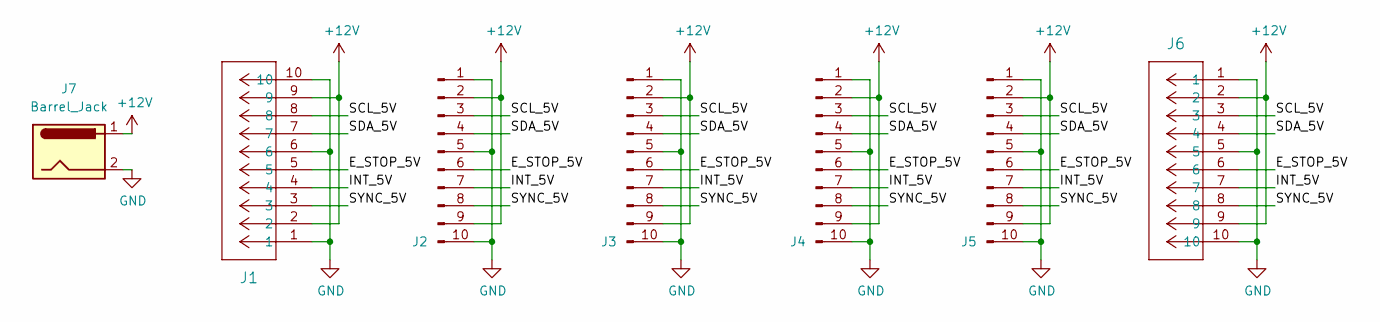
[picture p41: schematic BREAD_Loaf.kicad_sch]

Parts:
J1: PPPC101LGBN-RC; 1x10 RA Male Header 2.54mm Pitch
J2, J3, J4, J5: Conn_01x10_Male; BREAD 10-Pin Connector
J6: PPPC101LGBN-RC; PinSocket_1x10_P2.54mm_Horizontal
J7: Barrel_Jack; BarrelJack_CUI_PJ-063AH_Horizontal

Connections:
+12V: J1.2, J1.9, J2.2, J2.9, J3.2, J3.9, J4.2, J4.9, J5.2, J5.9, J6.2, J6.9, J7.1
/E_STOP_5V: J1.5, J2.6, J3.6, J4.6, J5.6, J6.6
/INT_5V: J1.4, J2.7, J3.7, J4.7, J5.7, J6.7
/SCL_5V: J1.8, J2.3, J3.3, J4.3, J5.3, J6.3
/SDA_5V: J1.7, J2.4, J3.4, J4.4, J5.4, J6.4
/SYNC_5V: J1.3, J2.8, J3.8, J4.8, J5.8, J6.8
GND: J1.1, J1.6, J1.10, J2.1, J2.5, J2.10, J3.1, J3.5, J3.10, J4.1, J4.5, J4.10, J5.1, J5.5, J5.10, J6.1, J6.5, J6.10, J7.2

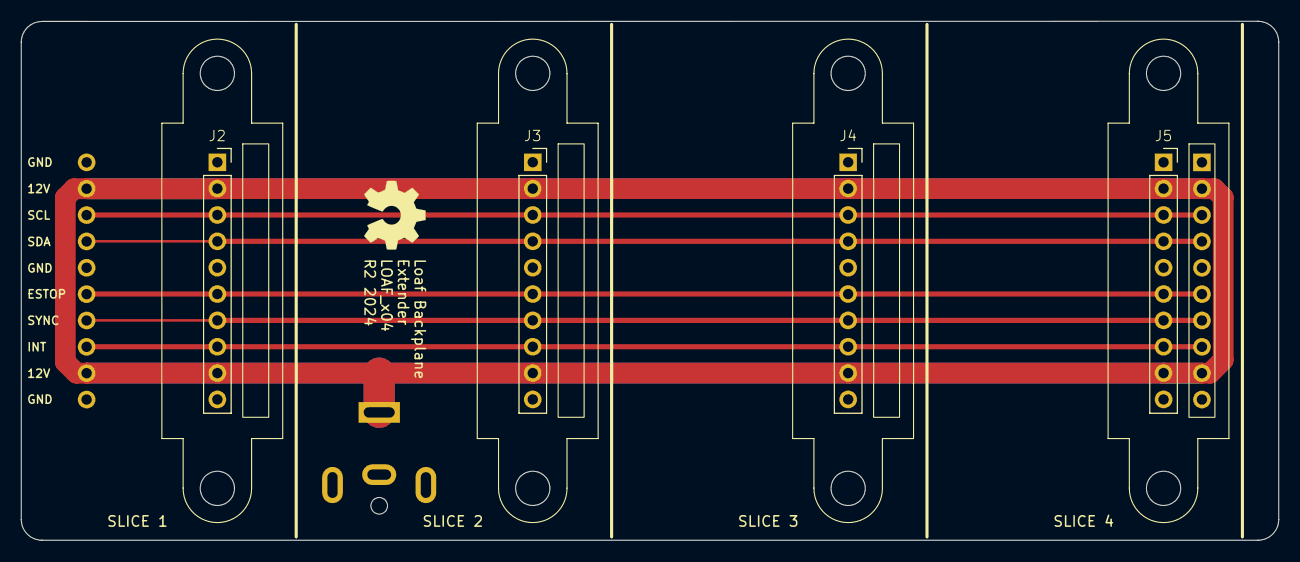
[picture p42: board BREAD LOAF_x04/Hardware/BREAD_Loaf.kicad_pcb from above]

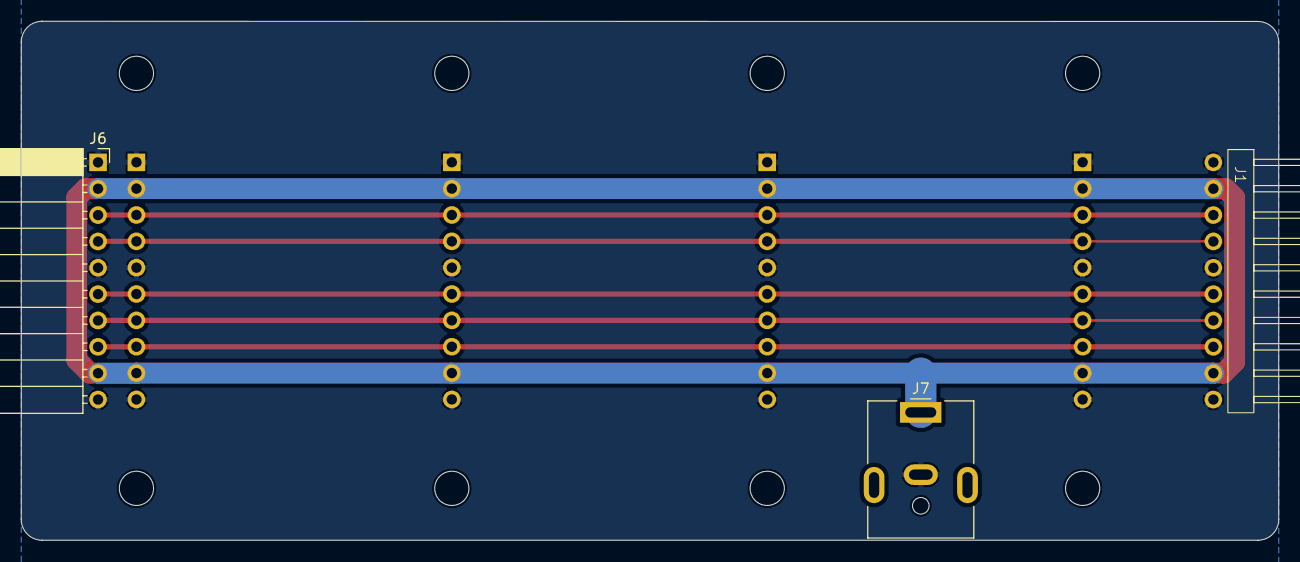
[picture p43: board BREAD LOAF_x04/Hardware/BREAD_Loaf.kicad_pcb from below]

Board: 2 copper layers, 121.2 x 50.0 mm, 8 parts (3 on the bottom side), 7 nets.

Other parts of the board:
Logo1: Logo_Open_Hardware_Small; OSHW-Symbol_6.7x6mm_SilkScreen

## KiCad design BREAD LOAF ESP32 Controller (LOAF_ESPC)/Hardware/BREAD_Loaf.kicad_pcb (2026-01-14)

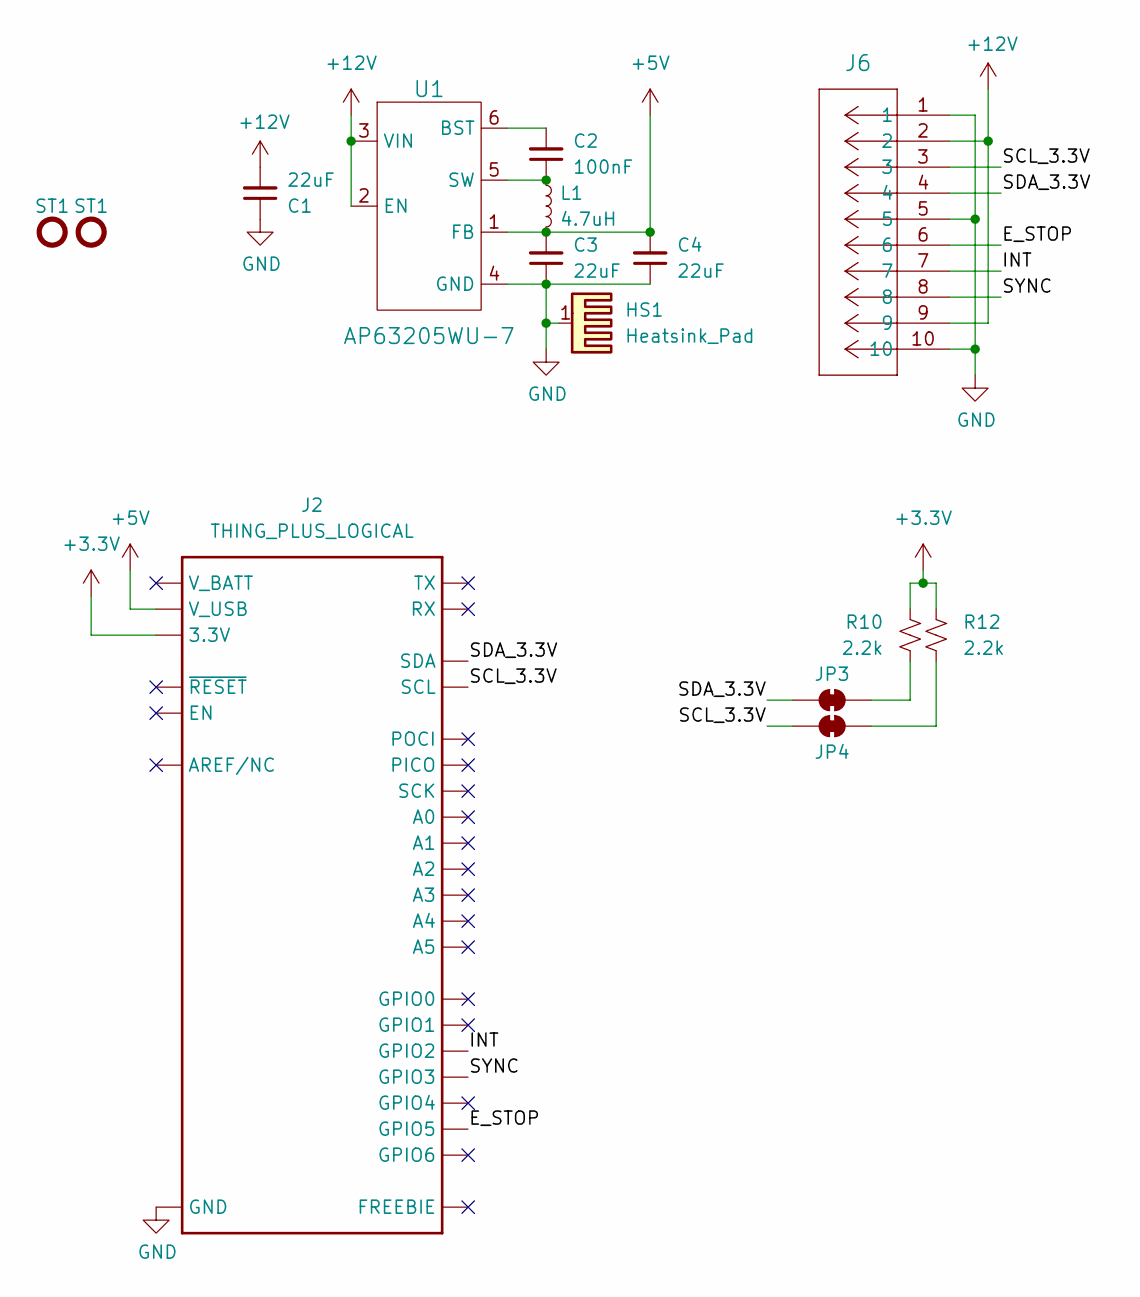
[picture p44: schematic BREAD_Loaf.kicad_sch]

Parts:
C1, C3, C4: 22uF; C_1206_3216Metric
C2: 100nF; C_1206_3216Metric
HS1: Heatsink_Pad; Thermal Pad
J2: THING_PLUS_LOGICAL; ESP_THING_PLUS
J6: PPPC101LGBN-RC; PinSocket_1x10_P2.54mm_Horizontal
JP3, JP4: SMT-JUMPER_2_NC_TRACE_SILK
L1: 4.7uH; L_1210_3225Metric
R10, R12: 2.2k; R_0603_1608Metric
ST1: Stand_off; STAND-OFF
U1: AP63205WU-7; TSOT-23-6

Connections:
+3.3V: J2.27 (3.3V), R10.1, R12.1
+5V: C3.2, C4.2, J2.10 (V_USB), L1.2; also elsewhere on the board
+12V: C1.2, J6.2, J6.9; also elsewhere on the board
/E_STOP: J2.4 (GPIO5), J6.6
/INT: J2.7 (GPIO2), J6.7
/SCL_3.3V: J2.2 (SCL), J6.3, JP4.2 (B)
/SDA_3.3V: J2.1 (SDA), J6.4, JP3.2 (B)
/SYNC: J2.6 (GPIO3), J6.8
GND: C1.1, C3.1, C4.1, HS1.1, J2.25 (GND), J6.1, J6.5, J6.10; also elsewhere on the board
unnamed: JP3.1 (A), R10.2
unnamed: JP4.1 (A), R12.2
unnamed 11: C2.2; also elsewhere on the board
unnamed 12: C2.1, L1.1; also elsewhere on the board

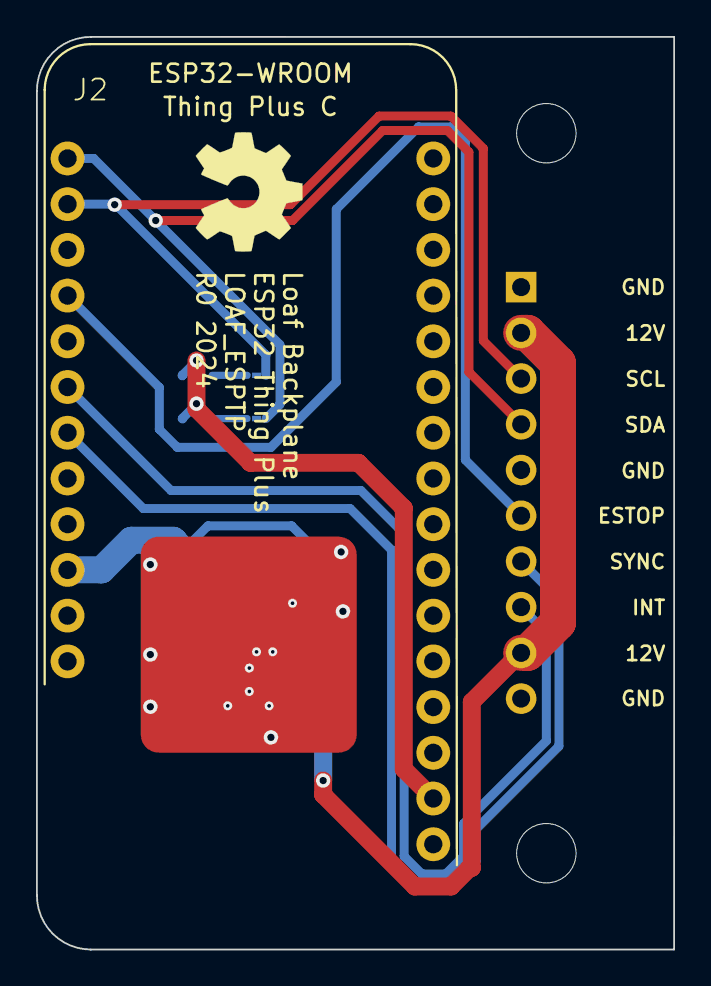
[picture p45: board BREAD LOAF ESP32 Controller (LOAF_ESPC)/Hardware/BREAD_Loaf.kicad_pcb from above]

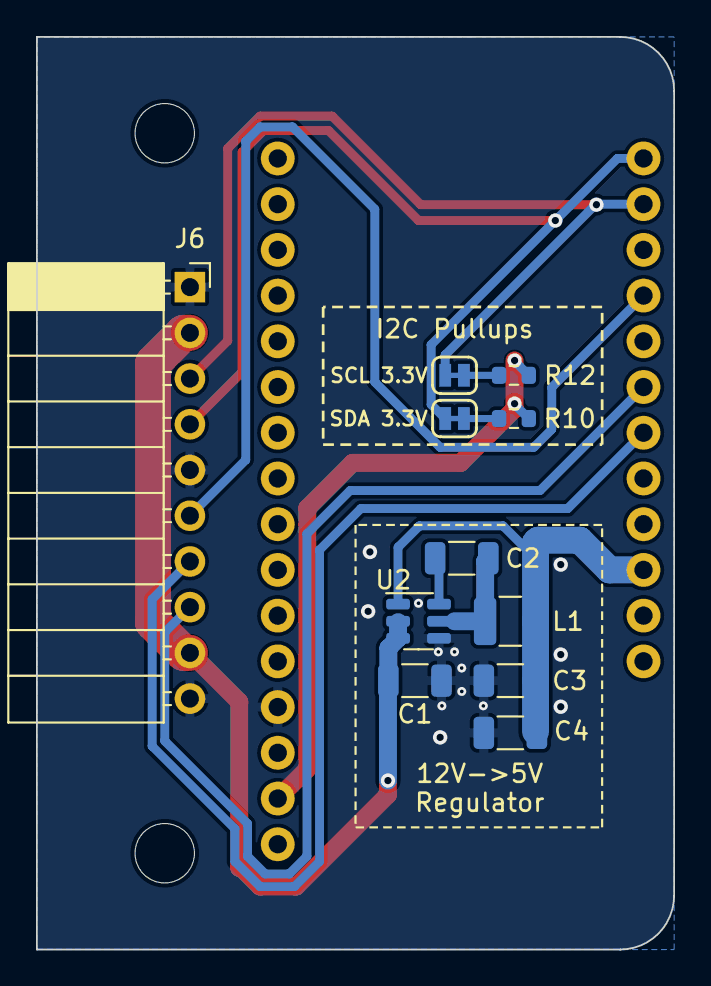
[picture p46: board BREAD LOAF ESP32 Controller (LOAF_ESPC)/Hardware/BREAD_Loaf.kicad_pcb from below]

Board: 2 copper layers, 35.4 x 50.7 mm, 16 parts (11 on the bottom side), 13 nets.

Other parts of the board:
Logo1: Logo_Open_Hardware_Small; OSHW-Symbol_6.7x6mm_SilkScreen
ST2: Stand_off; STAND-OFF
U2: AP63205WU-7; TSOT-23-6

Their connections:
+5V: U2.1 (FB); also elsewhere on the board
+12V: U2.2 (EN), U2.3 (VIN); also elsewhere on the board
GND: U2.4 (GND); also elsewhere on the board
unnamed 11: U2.6 (BST); also elsewhere on the board
unnamed 12: U2.5 (SW); also elsewhere on the board

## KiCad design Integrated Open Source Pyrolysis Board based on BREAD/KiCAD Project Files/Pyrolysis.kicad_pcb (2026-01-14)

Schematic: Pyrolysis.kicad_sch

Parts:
A1, A2, A3, A4, A5: Arduino_Nano_v3.x; Arduino_Nano
C1, C2, C3, C4, C8, C9, C12, C13, C14, C15, C16: 0.01 uF; C_1206_3216Metric_Pad1.33x1.80mm_HandSolder
C5, C10, C11: 10uF; C_1206_3216Metric_Pad1.33x1.80mm_HandSolder
C6, C7, C17: 10 nF; C_1206_3216Metric_Pad1.33x1.80mm_HandSolder
D1, D2, D3, D4, D5, D6, D7, D8, D9, D10: General_Purpose_Diode; D_DO-35_SOD27_P7.62mm_Horizontal; Part # 1N914BWS
F1, F2, F3, F4, F5, F6, F7, F8, F9, F10: 10A; Fuse_Holder; Part # 3522-2
FB1, FB2, FB3, FB4, FB5, FB6, FB7, FB8, FB9, FB10, FB11, FB12, FB13, FB14, FB15, FB16, FB17, FB18, FB19, FB20, FB21, FB22: Ferrite_Bead_Small; R_1206_3216Metric_Pad1.30x1.75mm_HandSolder
H1, H2, H3, H4: MountingHole; MountingHole_3.2mm_M3_DIN965_Pad
J1, J2, J3, J4, J5, J6, J7, J9, J11, J12, J15, J16, J17, J21, J22, J23, J27, J28, J29, J30, J32, J33, J34, J36, J37, J39, J40, J41, J43, J44, J45, J47, J48: Term_2; TerminalBlock_Phoenix_MKDS-1,5-2_1x02_P5.00mm_Horizontal; Part # 1935161
J8: Conn_01x03_Male; PinSocket_1x03_P2.54mm_Vertical
J10: Screw_Terminal_01x04; TerminalBlock_TE_282834-4_1x04_P2.54mm_Horizontal
J13: Conn_01x03_Male; PinHeader_1x03_P2.54mm_Vertical
J26: Barrel_Jack; BarrelJack_CUI_PJ-102AH_Horizontal
K1, K2, K3, K4, K5, K6, K7, K8, K9, K10: G5Q-1; Relay_SPDT_Omron-G5Q-1
R1: 2.2 k; R_1206_3216Metric_Pad1.30x1.75mm_HandSolder
U1, U4, U5, U8, U11, U14, U16, U18, U20, U22: TCMT1100; SOP-4_4.4x2.6mm_P1.27mm
U2, U3, U6, U7, U10, U13, U15, U17, U19, U21, U23: MAX6675ISA+; SO08-MAX6675
U12: AP1117-50; SOT-223-3_TabPin2
U24: LMD18200; TO-220-11_P3.4x5.08mm_StaggerOdd_Lead4.85mm_Vertical

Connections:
+5V: A1.27 (+5V), A2.27 (+5V), A3.27 (+5V), A4.27 (+5V), A5.27 (+5V), C11.1, J10.3, U2.4 (VCC), U3.4 (VCC), U6.4 (VCC), U7.4 (VCC), U10.4 (VCC), U12.2 (VO), U13.4 (VCC), U15.4 (VCC), U17.4 (VCC), U19.4 (VCC), U21.4 (VCC), U23.4 (VCC)
+12V: C10.1, F1.2, F2.2, F3.2, F4.2, F5.2, F6.2, F7.2, F8.2, F9.2, F10.2, J8.2, J26.1, U12.3 (VI)
/3V3: A3.17 (3V3)
/A1: A3.19 (A0), J10.1
/B1: A3.20 (A1), J10.2
/BR1: A3.9 (D6), U24.4 (BRAKE)
/CLK1: A2.16 (D13), U3.5 (SCK), U7.5 (SCK), U10.5 (SCK)
/CLK2: A4.16 (D13), U13.5 (SCK), U15.5 (SCK), U17.5 (SCK)
/CLK3: A5.16 (D13), U19.5 (SCK), U21.5 (SCK), U23.5 (SCK)
/CLK4: A1.16 (D13), U2.5 (SCK), U6.5 (SCK)
/CSEN1: A3.25 (A6), C17.1, R1.1, U24.8 (CURRENT_SENSE_OUTPUT)
/CUST1: J8.1, J11.1
/DATA1: A2.15 (D12), U3.7 (SO), U7.7 (SO), U10.7 (SO)
/DATA2: A4.15 (D12), U13.7 (SO), U15.7 (SO), U17.7 (SO)
/DATA3: A5.15 (D12), U19.7 (SO), U21.7 (SO), U23.7 (SO)
/DATA4: A1.15 (D12), U2.7 (SO), U6.7 (SO)
/DIR1: A3.10 (D7), U24.3 (DIRECTION)
/I2C_CLK: A1.24 (A5), A2.24 (A5), A3.24 (A5), A4.24 (A5), A5.24 (A5), J13.2
/I2C_DAT: A1.23 (A4), A2.23 (A4), A3.23 (A4), A4.23 (A4), A5.23 (A4), J13.1
/MC1: A3.12 (D9), U24.5 (PWM)
/PWM1: A2.8 (D5), U1.1
/PWM2: A2.9 (D6), U5.1
/PWM3: A2.10 (D7), U8.1
/PWM4: A4.8 (D5), U11.1
/PWM5: A4.9 (D6), U14.1
/PWM6: A4.10 (D7), U16.1
/PWM7: A5.8 (D5), U18.1
/PWM8: A5.9 (D6), U20.1
/PWM9: A5.10 (D7), U22.1
/PWM10: A1.10 (D7), U4.1
/SS1: A2.12 (D9), U3.6 (~CS)
/SS2: A2.13 (D10), U7.6 (~CS)
/SS3: A2.14 (D11), U10.6 (~CS)
/SS4: A4.12 (D9), U13.6 (~CS)
/SS5: A4.13 (D10), U15.6 (~CS)
/SS6: A4.14 (D11), U17.6 (~CS)
/SS7: A5.12 (D9), U19.6 (~CS)
/SS8: A5.13 (D10), U21.6 (~CS)
/SS9: A5.14 (D11), U23.6 (~CS)
/SS10: A1.13 (D10), U2.6 (~CS)
/SS11: A1.14 (D11), U6.6 (~CS)
/T+1: C1.1, FB1.1, U3.3 (T+)
/T+2: C4.1, FB5.1, U7.3 (T+)
/T+3: C8.1, FB7.1, U10.3 (T+)
/T+4: C9.1, FB9.1, U13.3 (T+)
/T+5: C12.1, FB11.1, U15.3 (T+)
/T+6: C13.1, FB13.1, U17.3 (T+)
/T+7: C14.1, FB15.1, U19.3 (T+)
/T+8: C15.1, FB17.1, U21.3 (T+)
/T+9: C16.1, FB19.1, U23.3 (T+)
/T+10: C2.1, FB3.1, U2.3 (T+)
/T+11: C3.1, FB21.1, U6.3 (T+)
/THRM1: A3.8 (D5), U24.9 (~THERMAL_FLAG_OUTPUT)
GND: A1.4 (GND), A1.29 (GND), A2.4 (GND), A2.29 (GND), A3.4 (GND), A3.29 (GND), A4.4 (GND), A4.29 (GND), A5.4 (GND), A5.29 (GND), C1.2, C2.2, C3.2, C4.2, C5.2, C8.2, C9.2, C10.2, C11.2, C12.2, C13.2, C14.2, C15.2, C16.2, C17.2, FB2.1, FB4.1, FB6.1, FB8.1, FB10.1, FB12.1, FB14.1, FB16.1, FB18.1, FB20.1, FB22.1, J6.2, J7.2, J10.4, J11.2, J13.3, J16.2, J22.2, J26.2, J28.2, J33.2, J37.2, J40.2, J44.2, J48.2, R1.2, U1.2, U1.3, U2.1 (GND), U2.2 (T-), U3.1 (GND), U3.2 (T-), U4.2, U4.3, U5.2, U5.3, U6.1 (GND), U6.2 (T-), U7.1 (GND), U7.2 (T-), U8.2, U8.3, U10.1 (GND), U10.2 (T-), U11.2, U11.3, U12.1 (GND), U13.1 (GND), U13.2 (T-), U14.2, U14.3, U15.1 (GND), U15.2 (T-), U16.2, U16.3, U17.1 (GND), U17.2 (T-), U18.2, U18.3, U19.1 (GND), U19.2 (T-), U20.2, U20.3, U21.1 (GND), U21.2 (T-), U22.2, U22.3, U23.1 (GND), U23.2 (T-), U24.7 (GND)
unnamed: C5.1, J8.3, U24.6 (VS)
unnamed: C6.1, J12.1, U24.2 (OUTPUT1)
unnamed: C6.2, U24.1 (BOOTSTRAP1)
unnamed: C7.1, U24.11 (BOOTSTRAP2)
unnamed: C7.2, J12.2, U24.10 (OUTPUT2)
unnamed: D1.1 (K), F1.1, K1.5
unnamed: D1.2 (A), K1.1, U1.4
unnamed: D2.1 (K), F2.1, K2.5
unnamed: D2.2 (A), K2.1, U4.4
unnamed: D3.1 (K), F3.1, K3.5
unnamed: D3.2 (A), K3.1, U5.4
unnamed: D4.1 (K), F4.1, K4.5
unnamed: D4.2 (A), K4.1, U8.4
unnamed: D5.1 (K), F5.1, K5.5
unnamed: D5.2 (A), K5.1, U11.4
unnamed: D6.1 (K), F6.1, K6.5
unnamed: D6.2 (A), K6.1, U14.4
unnamed: D7.1 (K), F7.1, K7.5
unnamed: D7.2 (A), K7.1, U16.4
unnamed: D8.1 (K), F8.1, K8.5
unnamed: D8.2 (A), K8.1, U18.4
unnamed: D9.1 (K), F9.1, K9.5
unnamed: D9.2 (A), K9.1, U20.4
unnamed: D10.1 (K), F10.1, K10.5
unnamed: D10.2 (A), K10.1, U22.4
unnamed: FB1.2, J1.2
unnamed: FB2.2, J1.1
unnamed: FB3.2, J2.2
unnamed: FB4.2, J2.1
unnamed: FB5.2, J9.2
unnamed: FB6.2, J9.1
unnamed: FB7.2, J17.2
unnamed: FB8.2, J17.1
unnamed: FB9.2, J23.2
unnamed: FB10.2, J23.1
unnamed: FB11.2, J30.2
unnamed: FB12.2, J30.1
unnamed: FB13.2, J34.2
unnamed: FB14.2, J34.1
unnamed: FB15.2, J29.2
unnamed: FB16.2, J29.1
unnamed: FB17.2, J41.2
unnamed: FB18.2, J41.1
unnamed: FB19.2, J45.2
unnamed: FB20.2, J45.1
unnamed: FB21.2, J3.2
unnamed: FB22.2, J3.1
unnamed: J4.1, K2.4
unnamed: J4.2, K2.3
unnamed: J5.1, K1.4
unnamed: J5.2, K1.3
unnamed: J6.1, K1.2
unnamed: J7.1, K2.2
unnamed: J15.1, K3.4
unnamed: J15.2, K3.3
unnamed: J16.1, K3.2
unnamed: J21.1, K4.4
unnamed: J21.2, K4.3
unnamed: J22.1, K4.2
unnamed: J27.1, K5.4
unnamed: J27.2, K5.3
unnamed: J28.1, K5.2
unnamed: J32.1, K6.4
unnamed: J32.2, K6.3
unnamed: J33.1, K6.2
unnamed: J36.1, K7.4
unnamed: J36.2, K7.3
unnamed: J37.1, K7.2
unnamed: J39.1, K8.4
unnamed: J39.2, K8.3
unnamed: J40.1, K8.2
unnamed: J43.1, K9.4
unnamed: J43.2, K9.3
unnamed: J44.1, K9.2
unnamed: J47.1, K10.4
unnamed: J47.2, K10.3
unnamed: J48.1, K10.2

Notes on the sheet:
Control Arduino 1
Thermocouples
Motor
Control Arduino 5
Control Arduino 2
Heater
Control Arduino 4
Heaters
Control Arduino 3
Core Components

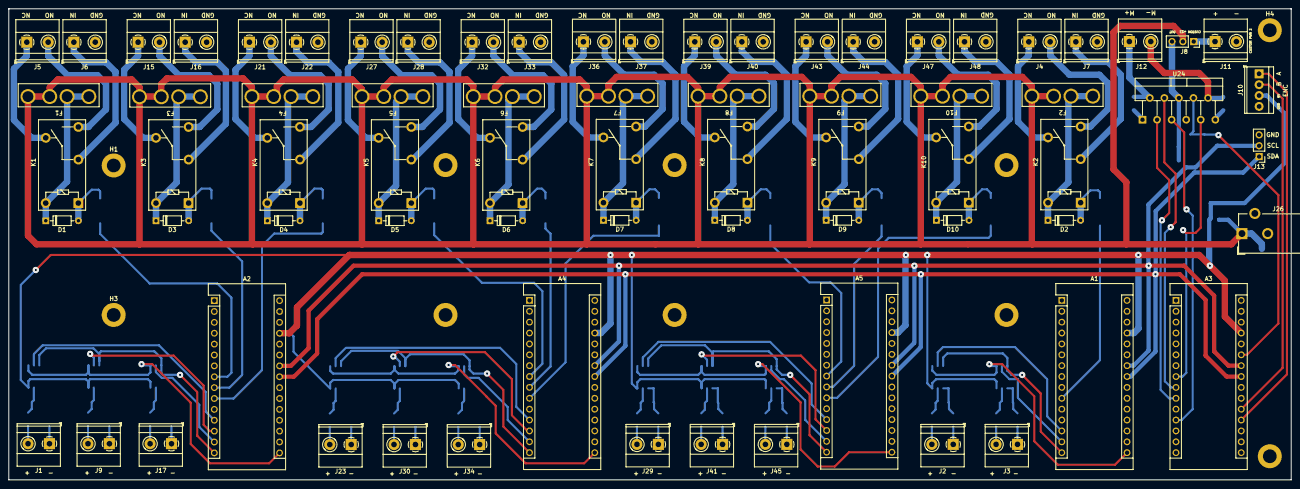
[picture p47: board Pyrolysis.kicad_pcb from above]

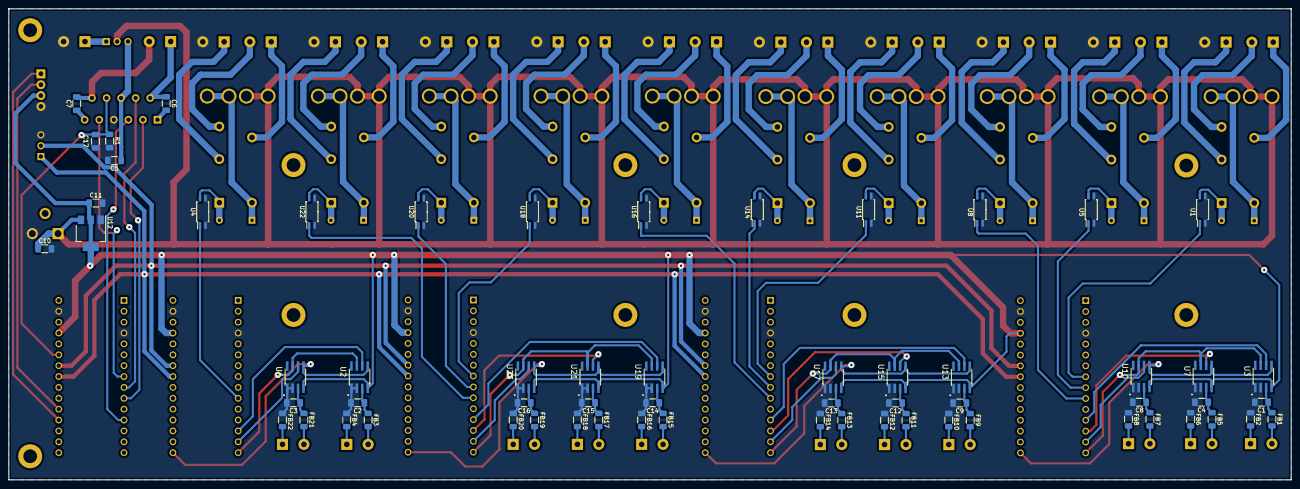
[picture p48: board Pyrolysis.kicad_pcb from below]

Board: 2 copper layers, 299.5 x 110.0 mm, 138 parts (62 on the bottom side), 130 nets.

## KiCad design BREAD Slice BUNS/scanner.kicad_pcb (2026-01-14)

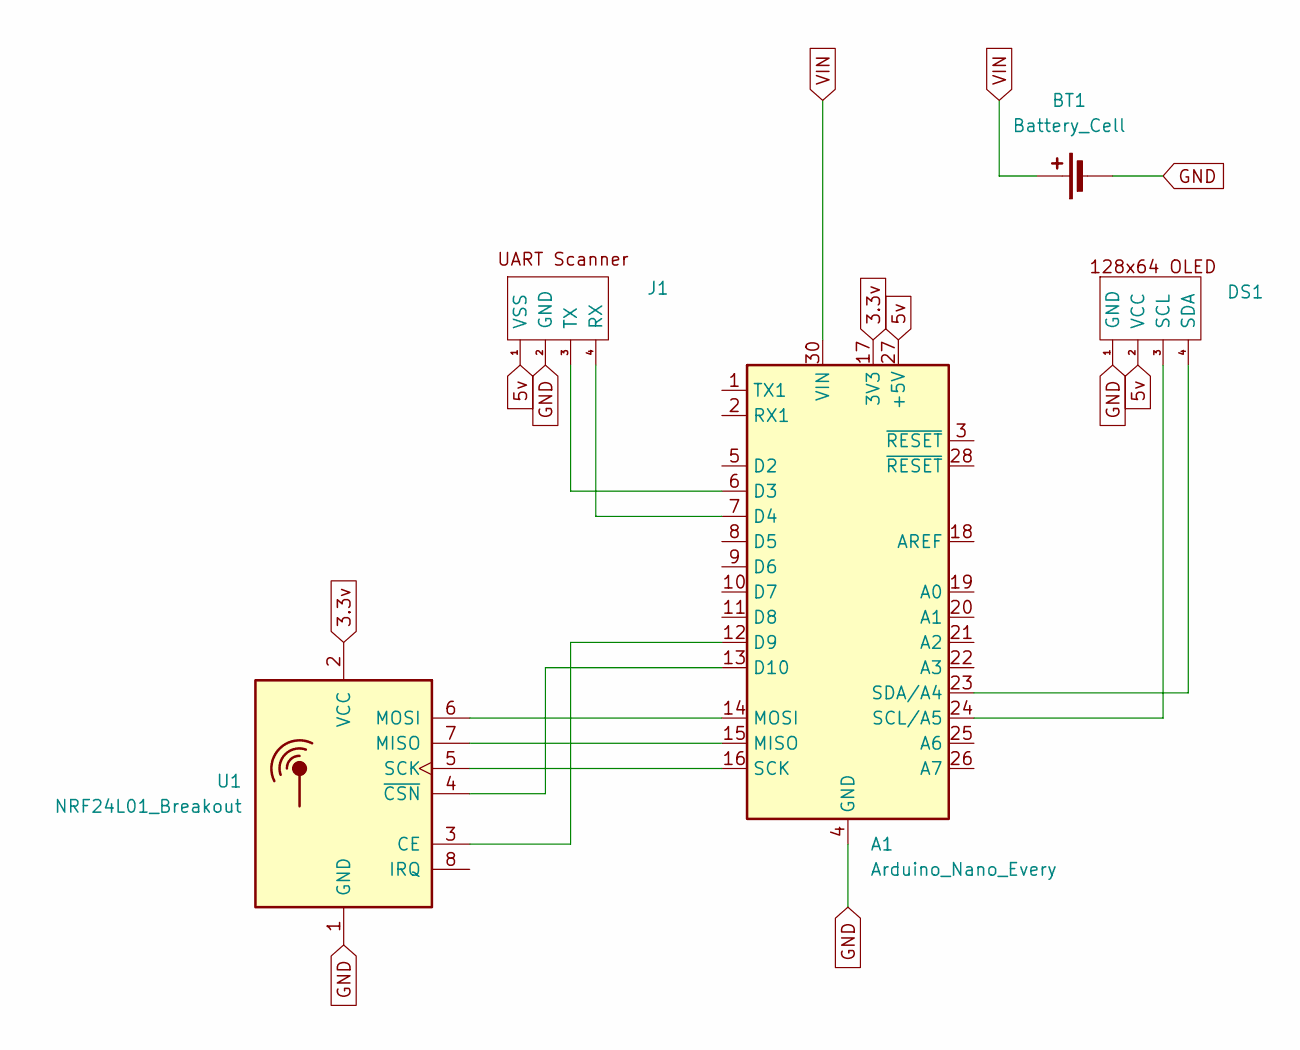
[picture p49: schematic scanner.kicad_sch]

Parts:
A1: Arduino_Nano_Every; Arduino_Nano
BT1: Battery_Cell; BatteryConnection
DS1: WireConnection
J1: WireConnection
U1: NRF24L01_Breakout; nRF24L01_Breakout

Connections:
3.3v: A1.17 (3V3), U1.2 (VCC)
5v: A1.27 (+5V), DS1.2 (VCC), J1.1 (VSS)
GND: A1.4 (GND), A1.29 (GND), BT1.2 (-), DS1.1 (GND), J1.2 (GND), U1.1 (GND)
unnamed: A1.6 (D3), J1.3 (TX)
unnamed: A1.7 (D4), J1.4 (RX)
unnamed: A1.12 (D9), U1.3 (CE)
unnamed: A1.13 (D10), U1.4 (~CSN)
unnamed: A1.15 (MISO), U1.7 (MISO)
unnamed: A1.14 (MOSI), U1.6 (MOSI)
unnamed: A1.16 (SCK), U1.5 (SCK)
unnamed: A1.24 (SCL/A5), DS1.3 (SCL)
unnamed: A1.23 (SDA/A4), DS1.4 (SDA)
VIN: A1.30 (VIN), BT1.1 (+)


Board: 2 copper layers, 60.5 x 41.5 mm, 5 parts (0 on the bottom side), 13 nets.

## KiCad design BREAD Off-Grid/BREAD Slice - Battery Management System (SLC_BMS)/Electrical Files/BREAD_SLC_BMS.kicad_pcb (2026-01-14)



Board: 2 copper layers, 70.0 x 100.0 mm, 53 parts (2 on the bottom side), 34 nets.

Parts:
0.5A1, 1.5A1: SOLDERJUMPER; SOLDERJUMPER_ARROW_NOPASTE
1A1: SOLDERJUMPERCLOSED; SOLDERJUMPER_CLOSEDWIRE
A1: Arduino_Nano_v3.x; Arduino_Nano
BATT1: JST 2PH; JST_S2B-PH-K-S(LF)(SN)
C1, C2, C7, C8: 10uF; 0805-NO
C3, C6: 22uF; 0805-NO
C4, C5: C; 0805-NO
Cff1: 3.3nF; C_1206_3216Metric_Pad1.33x1.80mm_HandSolder
Cin1: 680uF; CP_Radial_D12.5mm_P5.00mm
Cout1: 470uF; CP_Radial_D12.5mm_P5.00mm
D1, D2: SK34A; SMADIODE
D3, D6: D_Schottky; D_SMA_Handsoldering
D4: RED; CHIPLED_0603
D5: GREEN; CHIPLED_0603
H1, H2, H3, H4: MountingHole; MountingHole_3.2mm_M3_DIN965_Pad
J1: Conn_01x10_Female; PinSocket_1x10_P2.54mm_Horizontal
J2: USB_B_Micro; USB_Micro-B_GCT_USB3076-30-A
J3, J4, J5, J6: Screw_Terminal_01x02; TerminalBlock_Pheonix_MKDS1.5-2pol
L1: 22uH; L_Taiyo-Yuden_NR-50xx_HandSoldering
L2: 53uH; L_Toroid_Vertical_L21.6mm_W11.4mm_P7.62mm_Pulse_KM-3
Logo1: Logo_Open_Hardware_Small; OSHW-Symbol_6.7x6mm_SilkScreen
R1: 590; 0603-NO
R2, R4: 1K; 0603-NO
R3: 2K; 0603-NO
R5, R9, R10, R11: 10K; 0603-NO
R6: 1k; R_1206_3216Metric_Pad1.30x1.75mm_HandSolder
R7: 39k; 0603-NO
R8: 2.2k; 0603-NO
R12: 4.7k; R_1206_3216Metric_Pad1.30x1.75mm_HandSolder
SJ2: SOLDERJUMPER_2WAY; SOLDERJUMPER_2WAY_OPEN_NOPASTE
THERM1: SOLDERJUMPERCLOSED; SOLDERJUMPER_CLOSEDWIRE
U1: MT3608; SOT-23-6
U2: LM2596S-ADJ; TO-220-5_P3.4x3.7mm_StaggerOdd_Lead3.8mm_Vertical
X1: BQ24074; QFN16_3MM
locked: SOLDERJUMPER_2WAY; SOLDERJUMPER_2WAY_OPEN_NOPASTE

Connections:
/CHGI: A1.10 (D7), D4.A
/CHG_EN: A1.12 (D9), X1.4 (~CE)
/EN1: X1.6 (EN1), locked.2
/EN2: SJ2.2, X1.5 (EN2)
/E_STOP: A1.5 (D2), J1.6
/I2C_CLK: A1.24 (A5), J1.3
/I2C_DAT: A1.23 (A4), J1.4
/ILIM: R4.1, X1.12 (ILIM)
/INT: A1.6 (D3), J1.7
/ISET: A1.19 (A0), R1.1, R2.1, R3.1, X1.16 (ISET)
/ITERM: R5.1, X1.15 (ITERM)
/OUT: C3.1, C4.1, C5.1, L1.1, SJ2.1, U1.4 (EN), U1.5 (IN), X1.10 (OUT), X1.11 (OUT), locked.1
/PGOODI: A1.11 (D8), D5.A
/PWR: A1.30 (VIN), C6.1, D3.1 (K), J1.2, J1.9, J3.2, R7.1
/SYNC: A1.7 (D4), J1.8
/THERM: J5.2, THERM1.2, X1.1 (TS)
/Vmotor: Cin1.1, J6.2, U2.1 (VIN)
/~CHG: A1.8 (D5), X1.9 (~CHG)
/~PGOOD: A1.9 (D6), X1.7 (~PGOOD)
GND: 0.5A1.1, 1.5A1.1, 1A1.1, A1.4 (GND), A1.29 (GND), BATT1.2 (1), C1.2, C2.2, C3.2, C4.2, C5.2, C6.2, C7.2, C8.2, Cin1.2, Cout1.2, D6.2 (A), J1.1, J1.5, J1.10, J2.5 (GND), J3.1, J4.1, J5.1, J6.1, R4.2, R5.2, R6.1, R8.2, R9.2, R10.2, R11.2, SJ2.3, U1.2 (GND), U2.3 (GND), U2.5 (~ON/OFF), X1.8 (VSS), X1.14 (TMR), X1.THERMAL (VSS), locked.3
unnamed: 0.5A1.2, R3.2
unnamed: 1.5A1.2, R1.2
unnamed: 1A1.2, R2.2
unnamed: Cff1.1, R6.2, R12.1, U2.4 (FB)
unnamed: D1.A, J2.1 (VBUS)
unnamed: D2.A, J4.2
unnamed: D3.2 (A), L1.2, U1.1 (SW)
unnamed: D4.C, R10.1
unnamed: D5.C, R11.1
unnamed: D6.1 (K), L2.1, U2.2 (OUT)
unnamed: R7.2, R8.1, U1.3 (FB)
unnamed: R9.1, THERM1.1
VBUS: C1.1, C2.1, Cff1.2, Cout1.1, D1.C, D2.C, L2.2, R12.2, X1.13 (IN)
VLIPO: BATT1.1 (2), C7.1, C8.1, X1.2 (BAT), X1.3 (BAT)

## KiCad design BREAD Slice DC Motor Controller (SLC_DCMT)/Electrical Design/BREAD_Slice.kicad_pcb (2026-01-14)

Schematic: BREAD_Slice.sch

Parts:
A1: Arduino_Nano_v3.x; Arduino_Nano
C1, C2, C3, C4: 10uF_t; C_2312; Part # T491C106K025AT
C5, C6, C7, C8, C9, C10: 10 nF; C_1206_3216Metric_Pad1.33x1.80mm_HandSolder
H1, H2, H3, H4: MountingHole; MountingHole_3.2mm_M3_DIN965_Pad
J1: Conn_01x10_Female; PinSocket_1x10_P2.54mm_Horizontal
J2, J3: Screw_Terminal_01x04; TerminalBlock_TE_282834-4_1x04_P2.54mm_Horizontal
J4, J5: Conn_01x03_Male; PinSocket_1x03_P2.54mm_Vertical
J6, J7, J8, J9: Screw_Terminal_01x02; TerminalBlock_TE_282834-2_1x02_P2.54mm_Horizontal
Logo1: Logo_Open_Hardware_Small; OSHW-Symbol_6.7x6mm_SilkScreen
R3, R4: 2.2 k; R_1206_3216Metric_Pad1.30x1.75mm_HandSolder
U1, U2: LMD18200; TO-220-11_P3.4x5.08mm_StaggerOdd_Lead4.85mm_Vertical

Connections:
+5V: A1.27 (+5V), C2.1, J2.3, J3.3; also elsewhere on the board
+12V: A1.30 (VIN), C1.1, J1.2, J1.9, J4.2, J5.2; also elsewhere on the board
/A1: A1.19 (A0), J2.1; also elsewhere on the board
/A2: A1.21 (A2), J3.1; also elsewhere on the board
/B1: A1.20 (A1), J2.2; also elsewhere on the board
/B2: A1.22 (A3), J3.2; also elsewhere on the board
/BR1: A1.14 (D11), U1.4 (BRAKE); also elsewhere on the board
/BR2: A1.10 (D7), U2.4 (BRAKE); also elsewhere on the board
/CSEN1: A1.25 (A6), C10.1, R3.1, U1.8 (CURRENT_SENSE_OUTPUT); also elsewhere on the board
/CSEN2: A1.26 (A7), C9.1, R4.1, U2.8 (CURRENT_SENSE_OUTPUT); also elsewhere on the board
/CUST1: J4.1, J8.1
/CUST2: J5.1, J9.1
/DIR1: A1.12 (D9), U1.3 (DIRECTION); also elsewhere on the board
/DIR2: A1.8 (D5), U2.3 (DIRECTION); also elsewhere on the board
/E_STOP: A1.5 (D2), J1.6; also elsewhere on the board
/I2C_CLK: A1.24 (A5), J1.3; also elsewhere on the board
/I2C_DAT: A1.23 (A4), J1.4; also elsewhere on the board
/INT: A1.6 (D3), J1.7; also elsewhere on the board
/MC1: A1.13 (D10), U1.5 (PWM); also elsewhere on the board
/MC2: A1.9 (D6), U2.5 (PWM); also elsewhere on the board
/SYNC: A1.7 (D4), J1.8; also elsewhere on the board
/THRM1: A1.15 (D12), U1.9 (~THERMAL_FLAG_OUTPUT); also elsewhere on the board
/THRM2: A1.11 (D8), U2.9 (~THERMAL_FLAG_OUTPUT); also elsewhere on the board
GND: A1.4 (GND), A1.29 (GND), C1.2, C2.2, C3.2, C4.2, C9.2, C10.2, J1.1, J1.5, J1.10, J2.4, J3.4, J8.2, J9.2, R3.2, R4.2, U1.7 (GND), U2.7 (GND); also elsewhere on the board
unnamed 24: A1.1 (D1/TX); also elsewhere on the board
unnamed 25: A1.2 (D0/RX); also elsewhere on the board
unnamed 26: A1.3 (~RESET); also elsewhere on the board
unnamed 27: A1.16 (D13); also elsewhere on the board
unnamed 28: A1.17 (3V3); also elsewhere on the board
unnamed 29: A1.18 (AREF); also elsewhere on the board
unnamed 30: A1.28 (~RESET); also elsewhere on the board
unnamed: C3.1, J4.3, U1.6 (VS)
unnamed: C4.1, J5.3, U2.6 (VS)
unnamed: C5.1, J6.1, U1.2 (OUTPUT1)
unnamed: C5.2, U1.1 (BOOTSTRAP1)
unnamed: C6.1, U1.11 (BOOTSTRAP2)
unnamed: C6.2, J6.2, U1.10 (OUTPUT2)
unnamed: C7.1, J7.1, U2.2 (OUTPUT1)
unnamed: C7.2, U2.1 (BOOTSTRAP1)
unnamed: C8.1, U2.11 (BOOTSTRAP2)
unnamed: C8.2, J7.2, U2.10 (OUTPUT2)

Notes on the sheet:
Core Slice Components



Board: 2 copper layers, 70.0 x 100.0 mm, 30 parts (12 on the bottom side), 41 nets.

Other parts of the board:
A1#2: Arduino_Nano_v3.x; Arduino_Nano

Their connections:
+5V: A1#2.27; also elsewhere on the board
+12V: A1#2.30; also elsewhere on the board
/A1: A1#2.19; also elsewhere on the board
/A2: A1#2.21; also elsewhere on the board
/B1: A1#2.20; also elsewhere on the board
/B2: A1#2.22; also elsewhere on the board
/BR1: A1#2.14; also elsewhere on the board
/BR2: A1#2.10; also elsewhere on the board
/CSEN1: A1#2.25; also elsewhere on the board
/CSEN2: A1#2.26; also elsewhere on the board
/DIR1: A1#2.12; also elsewhere on the board
/DIR2: A1#2.8; also elsewhere on the board
/E_STOP: A1#2.5; also elsewhere on the board
/I2C_CLK: A1#2.24; also elsewhere on the board
/I2C_DAT: A1#2.23; also elsewhere on the board
/INT: A1#2.6; also elsewhere on the board
/MC1: A1#2.13; also elsewhere on the board
/MC2: A1#2.9; also elsewhere on the board
/SYNC: A1#2.7; also elsewhere on the board
/THRM1: A1#2.15; also elsewhere on the board
/THRM2: A1#2.11; also elsewhere on the board
GND: A1#2.4, A1#2.29; also elsewhere on the board
unnamed 24: A1#2.1; also elsewhere on the board
unnamed 25: A1#2.2; also elsewhere on the board
unnamed 26: A1#2.3; also elsewhere on the board
unnamed 27: A1#2.16; also elsewhere on the board
unnamed 28: A1#2.17; also elsewhere on the board
unnamed 29: A1#2.18; also elsewhere on the board
unnamed 30: A1#2.28; also elsewhere on the board

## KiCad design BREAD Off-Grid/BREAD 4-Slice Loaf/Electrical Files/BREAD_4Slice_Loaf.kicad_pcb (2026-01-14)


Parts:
A1: Arduino_Nano_v3.x; Arduino_Nano
C1, C2: 10uF_t; C_1206_3216Metric_Pad1.33x1.80mm_HandSolder; Part # T491C106K025AT
H1, H2, H3, H4: MountingHole; MountingHole_3.2mm_M3_DIN965_Pad
J1: Conn_01x03_Male; PinHeader_1x03_P2.54mm_Vertical
J2: Screw_Terminal_01x02; TerminalBlock_Phoenix_MKDS-1,5-2_1x02_P5.00mm_Horizontal
U1, U2, U3, U4: BREAD_Slice_Mounting
U9: CD74HC4050; DIP-16_W7.62mm_Socket_LongPads
U10: microSD_Connector; micro_SD_LOAF

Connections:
+5V: A1.27 (+5V), C2.1
+12V: A1.30 (VIN), C1.1, J2.1, U1.2 (+12V), U1.9 (+12V), U2.2 (+12V), U2.9 (+12V), U3.2 (+12V), U3.9 (+12V), U4.2 (+12V), U4.9 (+12V)
/3V3: A1.17 (3V3), U9.1 (Vcc), U10.4 (VDD)
/CLK: U9.6 (3Y), U10.5 (CLK)
/CLK5: A1.16 (D13), U9.7 (3A)
/CS: U9.2 (1Y), U10.2 (CS)
/CS5: A1.11 (D8), U9.3 (1A)
/DI: U9.4 (2Y), U10.3 (DI)
/DI5: A1.14 (D11), U9.5 (2A)
/DO: A1.15 (D12), U10.7 (DO)
/E_STOP: A1.5 (D2), U1.6 (E_STOP), U2.6 (E_STOP), U3.6 (E_STOP), U4.6 (E_STOP)
/I2C_CLK: A1.24 (A5), J1.2, U1.3 (I2C_CLK), U2.3 (I2C_CLK), U3.3 (I2C_CLK), U4.3 (I2C_CLK)
/I2C_DAT: A1.23 (A4), J1.3, U1.4 (I2C_DAT), U2.4 (I2C_DAT), U3.4 (I2C_DAT), U4.4 (I2C_DAT)
/INT: A1.6 (D3), U1.7 (INT), U2.7 (INT), U3.7 (INT), U4.7 (INT)
/SYNC: A1.7 (D4), U1.8 (SYNC), U2.8 (SYNC), U3.8 (SYNC), U4.8 (SYNC)
GND: A1.4 (GND), A1.29 (GND), C1.2, C2.2, J1.1, J2.2, U1.1 (GND), U1.5 (GND), U1.10 (GND), U2.1 (GND), U2.5 (GND), U2.10 (GND), U3.1 (GND), U3.5 (GND), U3.10 (GND), U4.1 (GND), U4.5 (GND), U4.10 (GND), U9.8 (GND), U9.9 (4A), U9.11 (5A), U9.14 (6A), U10.6 (GND), U10.10 (SHIELD)



Board: 2 copper layers, 139.1 x 200.0 mm, 16 parts (3 on the bottom side), 16 nets.

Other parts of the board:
Logo1: Logo_Open_Hardware_Small; OSHW-Symbol_6.7x6mm_SilkScreen

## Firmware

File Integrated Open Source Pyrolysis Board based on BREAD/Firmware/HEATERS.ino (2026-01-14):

#include <Wire.h>
#include "max6675.h"

#define PWM1  5
#define PWM2  6
#define PWM3  7

#define SS1   9
#define SS2   10
#define SS3   11
#define DATA1 12
#define CLK1  13

#define I2C_ADR 1 //Set this however you want

#define MAX_DUTY_CYCLE  10  // to prevent PID control from overheating coils (increase for slower heating systems)

// initialize the Thermocouples
MAX6675 CH1(CLK1, SS1, DATA1);
MAX6675 CH2(CLK1, SS2, DATA1);
MAX6675 CH3(CLK1, SS3, DATA1);


typedef union //Define a float that can be broken up and sent via I2C
{
  float number;
  uint8_t bytes[4];
} FLOATUNION_t;

FLOATUNION_t RX;

byte commandSelect[3];
byte tempSelect = 0;  // select thermocouple to measure
byte heaterSelect = 0;  // select heater to control
float dutySelect1 = 0;  // select duty cycle for heater1
float dutySelect2 = 0;  // select duty cycle for heater2
float dutySelect3 = 0;  // select duty cycle for heater3

int onTime1;
int offTime1;

int onTime2;
int offTime2;

int onTime3;
int offTime3;

int period = 1000; // duty cycle period in milliseconds

bool heater1On = false;
bool heater2On = false;
bool heater3On = false;

long curTime1 = 0;
long curTime2 = 0;
long curTime3 = 0;

long lastUpdate = 0;
long updateInterval = 1000;  // in milliseconds

void setup() {
  // put your setup code here, to run once:
  Serial.begin(9600);

  pinMode(PWM1, OUTPUT);
  pinMode(PWM2, OUTPUT);
  pinMode(PWM3, OUTPUT);

  Wire.begin(I2C_ADR);
  Wire.onRequest(requestEvent);
  Wire.onReceive(receiveEvent);

  // wait for MAX chip to stabilize
  delay(500);
  
  curTime1 = millis();
  curTime2 = millis();
  curTime3 = millis();
  
  onTime1 = period*dutySelect1/100;
  onTime2 = period*dutySelect2/100;
  onTime3 = period*dutySelect3/100;
  
  offTime1 = period-onTime1;
  offTime2 = period-onTime2;
  offTime3 = period-onTime3;
}

void loop() {
  // put your main code here, to run repeatedly:

    // Heater 1 --------------------------------------------------------
    if(dutySelect1 != 0){  // only run if duty cycle is nonzero
      onTime1 = period*dutySelect1/100;
      offTime1 = period-onTime1;
      if(!heater1On && millis() - curTime1 >= offTime1){  //wait for off cycle to finish
        curTime1 = millis();
        digitalWrite(PWM1, HIGH);  //turn on
        Serial.println("1 -> ON");
        heater1On = true;
      }
      else if(heater1On && millis() - curTime1 >= onTime1){ //wait for on cycle to finish
        curTime1 = millis();
        digitalWrite(PWM1, LOW);   //turn off
        Serial.println("1 -> OFF");
        heater1On = false;
      }
    }
    else if (heater1On){
        heater1On = false;
        digitalWrite(PWM1, LOW);   //turn off
        Serial.println("1 -> OFF");
    }
      
    // Heater 2 --------------------------------------------------------
    if(dutySelect2 != 0){  // only run if duty cycle is nonzero
      onTime2 = period*dutySelect2/100;
      offTime2 = period-onTime2;
      if(!heater2On && millis() - curTime2 >= offTime2){  //wait for off cycle to finish
        curTime2 = millis();
        digitalWrite(PWM2, HIGH);  //turn on
        Serial.println("2 -> ON");
        heater2On = true;
      }
      else if(heater2On && millis() - curTime2 >= onTime2){ //wait for on cycle to finish
        curTime2 = millis();
        digitalWrite(PWM2, LOW);   //turn off
        Serial.println("2 -> OFF");
        heater2On = false;
      }
    }
    else if (heater2On){
        heater2On = false;
        digitalWrite(PWM2, LOW);   //turn off
        Serial.println("2 -> OFF");
    }
      
    // Heater 3 --------------------------------------------------------
    if(dutySelect3 != 0){  // only run if duty cycle is nonzero
      onTime3 = period*dutySelect3/100;
      offTime3 = period-onTime3;
      if(!heater3On && millis() - curTime3 >= offTime3){  //wait for off cycle to finish
        curTime3 = millis();
        digitalWrite(PWM3, HIGH);  //turn on
        Serial.println("3 -> ON");
        heater3On = true;
      }
      else if(heater3On && millis() - curTime3 >= onTime3){ //wait for on cycle to finish
        curTime3 = millis();
        digitalWrite(PWM3, LOW);   //turn off
        Serial.println("3 -> OFF");
        heater3On = false;
      }
    }
    else if (heater3On){
        heater3On = false;
        digitalWrite(PWM3, LOW);   //turn off
        Serial.println("3 -> OFF");
    }
}

void requestEvent() {
  switch (tempSelect) {
    case 1:
      RX.number = CH1.readCelsius();  // reference a pointer instead
      break;
    case 2:
      RX.number = CH2.readCelsius();
      break;
    case 3:
      RX.number = CH3.readCelsius();
      break;
    default:
      RX.number = 0;
  }
  if(!isnan(RX.number)){
    for (int i = 0; i <= 3; i++)
    {
      Wire.write(RX.bytes[i]);
      Serial.print(RX.bytes[i]);
      Serial.print(", ");
    }
    Serial.print("-> Float: ");
    Serial.println(RX.number);
  }
  else{
    for (int i = 0; i <= 3; i++)
    {
      Wire.write(0);
      Serial.print(0);
      Serial.print(", ");
    }
    Serial.println();
  }
  commandSelect[1] = 0;
}

void receiveEvent(int howMany) {
  int i=0;
  while (Wire.available()) {
    commandSelect[i] = Wire.read();
    Serial.print(commandSelect[i]);
    Serial.print(", ");
    i++;
  }
  Serial.println();
  
  switch(commandSelect[0]){
    case 'T':
      tempSelect = commandSelect[1];  // wants temperature readings
      break;
    case 1:
      dutySelect1 = commandSelect[1];  // select heater to change duty cycle
      tempSelect = 0;
      break;
    case 2:
      dutySelect2 = commandSelect[1];  // select heater to change duty cycle
      tempSelect = 0;
      break;
    case 3:
      dutySelect3 = commandSelect[1];  // select heater to change duty cycle
      tempSelect = 0;
      break;
  }
  if(dutySelect1 > MAX_DUTY_CYCLE){
    dutySelect1 = MAX_DUTY_CYCLE;
  }
  if(dutySelect2 > MAX_DUTY_CYCLE){
    dutySelect2 = MAX_DUTY_CYCLE;
  }
  if(dutySelect3 > MAX_DUTY_CYCLE){
    dutySelect3 = MAX_DUTY_CYCLE;
  }
}

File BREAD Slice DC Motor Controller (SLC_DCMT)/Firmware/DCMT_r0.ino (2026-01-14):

#include <Wire.h>
//#include <SPI.h>

#define I2C_ADR 14 //Set this however you want

#define DIR1  5
#define MC1   6
#define BR1   7
#define DIR2  9
#define MC2   10
#define BR2   11

bool dir1 = 1;
bool dir2 = 1;
bool br1 = 0;
bool br2 = 0;

int pwm1, pwm2;

typedef union //Define a float that can be broken up and sent via I2C
{
 float number;
 uint8_t bytes[4];
} FLOATUNION_t;

FLOATUNION_t RX;

byte commandSelect[3];
int8_t speedSelect;
int8_t motor1Speed;
int8_t motor2Speed;
byte motorSelect;
bool changeParam = false;

int blinkPeriod = 1000;
long lastBlinkTime = 0;
bool blinkOn = false;

void setup() {
  // put your setup code here, to run once:
  pinMode(MC1, OUTPUT);
  pinMode(MC2, OUTPUT);
  pinMode(DIR1, OUTPUT);
  pinMode(DIR2, OUTPUT);
  pinMode(BR1, OUTPUT);
  pinMode(BR2, OUTPUT);
  pinMode(LED_BUILTIN, OUTPUT);

  Serial.begin(9600);
  Wire.begin(I2C_ADR);
  Wire.onReceive(receiveEvent);
  Wire.onRequest(requestEvent);
}

void loop() {
  if(millis() - lastBlinkTime >= blinkPeriod){
    lastBlinkTime = millis();
    if(blinkOn){
      digitalWrite(LED_BUILTIN, LOW);
      blinkOn = false;
    }
    else{
      digitalWrite(LED_BUILTIN, HIGH);
      blinkOn = true;
    }
  }
  if(changeParam){
    switch(motorSelect){
      case 1: // Motor 1 edit
        if(speedSelect == 0){
          br1 = 1;
          pwm1 = 0;
          Serial.println("Motor 1 brake");
        }
        else if(speedSelect < 0 && speedSelect >= -100){
          br1 = 0;
          dir1 = 0;
          speedSelect *= -1;
          pwm1 = map(speedSelect, 0, 100, 0, 255);
          Serial.print("Motor 1 back ");
          Serial.println(pwm1);
        }
        else if(speedSelect > 0 && speedSelect <= 100){
          br1 = 0;
          dir1 = 1;
          pwm1 = map(speedSelect, 0, 100, 0, 255);
          Serial.print("Motor 1 forward ");
          Serial.println(pwm1);
        }
        else{
          Serial.println("Invalid Entry, nothing will be changed");
        }
        break;
  
      case 2: // motor 2 edit
        if(speedSelect == 0){
          br2 = 1;
          pwm2 = 0;
          Serial.println("Motor 2 brake");
        }
        else if(speedSelect < 0 && speedSelect >= -100){
          br2 = 0;
          dir2 = 0;
          speedSelect *= -1;
          pwm2 = map(speedSelect, 0, 100, 0, 255);
          Serial.print("Motor 2 back ");
          Serial.println(pwm2);
        }
        else if(speedSelect > 0 && speedSelect <= 100){
          br2 = 0;
          dir2 = 1;
          pwm2 = map(speedSelect, 0, 100, 0, 255);
          Serial.print("Motor 2 forward ");
          Serial.println(pwm2);
        }
        else{
          Serial.println("Invalid Entry, nothing will be changed");
        }
        break;
        
      default:
        Serial.println("oopsie poopsie, that's not a command, silly");
        break;
    }
    digitalWrite(DIR1, dir1);
    analogWrite(MC1, pwm1);
    
    digitalWrite(DIR2, dir2);
    analogWrite(MC2, pwm2);

    changeParam = false;
  }
}

void requestEvent() {
  Serial.print("Sending: ");
  Serial.print(motor1Speed);
  Serial.print(", ");
  Serial.println(motor2Speed);

  Wire.write(motor1Speed);
  Wire.write(motor2Speed);
}

void receiveEvent(int howMany) {
  int i=0;
  while (Wire.available()) {
    commandSelect[i] = Wire.read();
    Serial.print(i);
    Serial.print("-> ");
    Serial.print(commandSelect[i]);
    Serial.print(", ");
    i++;
  }
  Serial.println();
  motorSelect = commandSelect[0];
  speedSelect = commandSelect[1];

  switch(motorSelect){
    case 1:
      motor1Speed = speedSelect;
      break;
    case 2:
      motor2Speed = speedSelect;
      break;
  }
  
  changeParam = true;
}

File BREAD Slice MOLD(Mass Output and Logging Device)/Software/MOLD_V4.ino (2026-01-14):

//MOLD 

#include <Wire.h> 
#include <LiquidCrystal_I2C.h>
#include <BfButton.h>
#include <HX711_ADC.h>
#include <EEPROM.h>

//States of device
bool Calibrate = false;
bool boot = false;
bool homeMenu = false;
bool editGoal = false;
bool settings = false;

//Rotary Encoder Setup data pins
const int RotaryBtn = PD6;//Rotary Encoder Button pin
#define outputA 7 //pin dt
#define outputB 8 //pin clk
//Rotary Encoder Button Constructor
BfButton btn(BfButton::STANDALONE_DIGITAL, RotaryBtn, true, LOW);
//Rotary Encoder Variables
volatile bool A = false;
volatile bool B = false;
int aState;
int aLastState;

//Load Cell HX11 pins
const int HX711_dout = 4; //mcu > HX711 dout pin
const int HX711_sck = 5; //mcu > HX711 sck pin
//HX711 constructor
HX711_ADC LoadCell(HX711_dout, HX711_sck);
//Scale Variables
const int calVal_eepromAdress = 0;
unsigned long t = 0;
float  weight;//weight seen on scale
double goal = 1000;//weight goal
double goalTol = 0.2;//20% tol
double WeightVsGoal;
float known_mass = 1000;

//I2C LCD Constructor Connect to SCL and SDA pins 
LiquidCrystal_I2C lcd(0x27,16,2); // set the LCD address to 0x27 for a 16 chars and 2 line display

//digital output of if weight is in tollerance 
const int inTolOut = 12;

//loadcell callabrate
bool notReady = true;

void setup() {
  // Screen Setup
  lcd.init(); //initialize the lcd
  lcd.backlight(); //open the backlight 
  //RotaryEncoder
  pinMode (outputA, INPUT);
  pinMode (outputB, INPUT);
  //buttons
  btn.onPress(pressHandler)
  .onDoublePress(pressHandler)
  .onPressFor(pressHandler, 1000);

  //Load Cell Start
  LoadCell.begin();
  //Set output pin for in tollarance 
  pinMode(inTolOut,OUTPUT);
  //Start Serial
  Serial.begin(57600);
  //start in boot
  boot = true;
}

void loop() {
  //Check for data LoadCell
  static boolean newDataReady = 0;
  if(LoadCell.update()){
    newDataReady = true;
  }
  //get value for new loadcelll load
  if(newDataReady){
    weight = LoadCell.getData();

    newDataReady = 0;
  }

  //Update the button
  btn.read();

  //Rotary Encoder Check for changes (rotation)
  aState = digitalRead(outputA);
    if(aState != aLastState ){
      if(digitalRead(outputB) != aState){ 
        
        //decrease by
        if(editGoal){
          goal = goal - 10;
        }
        
      }else{
        
        // increase by 
        if(editGoal){
          goal = goal +10;
        }
        
      }
    }
    aLastState = aState;

  //update screen
  const int serialPrintInterval = 500; //increase value to slow down serial print activity
  if (millis() > t + serialPrintInterval) {
      
    
  if(boot){
    lcd.setCursor(0,0); // set cursor to start of first line
    lcd.print("                ");//Clear LCD first line
    lcd.setCursor(0,1); // set cursor to start of first line
    lcd.print("                ");//Clear LCD Second line
    lcd.setCursor(0,0);
    lcd.println("BREAD MOLD      ");
    lcd.setCursor(0,1);
    lcd.println("Boot");
    calibrate();
    boot = false; 
    homeMenu = true;
  }
  if (homeMenu){
    lcd.setCursor(0,0); // set cursor to start of first line
    lcd.print("                ");//Clear LCD first line
    lcd.setCursor(0,1); // set cursor to start of first line
    lcd.print("                ");//Clear LCD Second line
    lcd.setCursor(0,0); // set cursor to start of first line
    lcd.print("Weight:");
    lcd.setCursor(8,0);
    lcd.print((double)weight);
    lcd.setCursor(0,1); // set cursor to start of first line
    lcd.print("W/G:");
    lcd.setCursor(5,1);
    WeightVsGoal = ((double)weight / goal)*100;
    lcd.print(WeightVsGoal);
    lcd.setCursor(15,1);
    lcd.print("%");
    //Check to tolarance
    if(WeightVsGoal>(100+(goalTol*100))){
      digitalWrite(inTolOut, HIGH);
    }else if(WeightVsGoal<(100-(goalTol*100))){
      digitalWrite(inTolOut, HIGH);
    }
    else{
      digitalWrite(inTolOut, LOW);
    }
  }
  if (editGoal){
    lcd.setCursor(0,0); // set cursor to start of first line
    lcd.print("                ");//Clear LCD first line
    lcd.setCursor(0,1); // set cursor to start of first line
    lcd.print("                ");//Clear LCD Second line
    lcd.setCursor(0,0); // set cursor to start of first line
    lcd.print("Set Goal");
    lcd.setCursor(0,1); // set cursor to start of first line
    lcd.print("Goal:");
    lcd.setCursor(6,1);
    lcd.print((double)goal);
  }
  if (settings){
    lcd.setCursor(0,0); // set cursor to start of first line
    lcd.print("                ");//Clear LCD first line
    lcd.setCursor(0,1); // set cursor to start of first line
    lcd.print("                ");//Clear LCD Second line
    lcd.setCursor(0,0); // set cursor to start of first line
    lcd.print("Single Back");
    lcd.setCursor(0,1); // set cursor to start of first line
    lcd.print("Hold Calibrate");
  }
  
    t = millis();
  }


}
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

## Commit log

2026-01-14 Commit initial collection
    [AAFT_BOM.csv, BOM.xlsx, BOM_AAFT.ods, BOM_CR10.csv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]
2026-01-14 Add additional SLICE and LOAF
    [BOM_LOAF_EXT_R2.ods, BREAD_Loaf-B_Cu.gbr, BREAD_Loaf-B_Mask.gbr, BREAD_Loaf-B_Paste.gbr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]
2026-04-06 Add Pressure Sensor Slice
    [BREAD_Slice.kicad_pcb]
